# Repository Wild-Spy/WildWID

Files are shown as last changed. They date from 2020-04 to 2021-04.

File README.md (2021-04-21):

# WildWID
An open-source active RFID system for wildlife research

## Requirements
Some device firmware is written in C and requires the AVR/Atmel Studio IDE - https://www.microchip.com/mplab/avr-support/avr-and-sam-downloads-archive

Some device firmware is written in C and requires the IAR Embedded Workbench for 8051 IDE - https://www.iar.com/iar-embedded-workbench/#!?architecture=8051

Programming software is written in Visual Basic and requires the Microsoft Visual Studio IDE - https://visualstudio.microsoft.com

## Repository Structure
The WildWID repository is organised around the two components of the WildWID system: tags and loggers. Within the `Logger` and `Tag` folders you will find two sub-folders:

* Device firmware: contains firmware for the respective device.
* Production: contains the schematics and bill of materials required for PCB fabrication.

Within the `PC_Software` folder you will find multiple sub-folders containing the enduser software required to configure, test, and deploy tags and loggers.

## Further Information
A more detailed overview of WildWID and its use in wildlife biology is covered in: 

Rafiq, K., Appleby, R.G., Edgar, J.P., Jordan, N.R., Radford, C., Smith, B., Dexter, C.E., Jones, D.N., Blacker, A.R.F., and Cochrane, M., 'WildWID: An open-source active RFID system for wildlife research', *Methods in Ecology and Evolution*, in publication.



## License
This project is licensed under the terms of the GNU General Public License v3.0. See [LICENSE](LICENSE) for details.

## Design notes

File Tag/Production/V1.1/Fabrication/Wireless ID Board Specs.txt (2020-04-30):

Wireless ID Board Specifications

Layers: 		4
Thickness: 		0.6mm
Blind/Burried Vias: 	No
Surface Finish:		HAL Pb/Sn
Copper Finish:		1oz
Solder Mask:		Both Sides
Silk Screen:		Both Sides
Min Trace:		6mil
Min Hole:		12mil
PCB Material:		FR4

Gerber Files:
Bottom Copper Layer 	- Wireless ID.GBL
Bottom Solder Mask 	- Wireless ID.GBS
Bottom Silkscreen 	- Wireless ID.GBO
Internal Plane 1	- Wireless ID.GP1
Internal Plane 2	- Wireless ID.GP2
Top Copper Layer	- Wireless ID.GTL
Top Solder Mask		- Wireless ID.GTS
Top Silkscreen		- Wireless ID.GTO
Board Outline		- Wireless ID.GKO

Also, for Solder Paste Stencils:
(Copies of these files are also included in the 'Assembly Files' folder)
Top Paste Layer		- Wireless ID.GTP
Bottom Paste Layer	- Wireless ID.GBP

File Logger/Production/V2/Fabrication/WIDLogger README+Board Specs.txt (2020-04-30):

Wireless ID Board Specifications

Layers: 		2
Thickness: 		1.6mm
Surface Finish:	HAL Pb/Sn
Copper Finish:	1oz
Solder Mask:	Both Sides
Silk Screen:	Top Only
Min Trace:		6mil
Min Hole:		12mil
PCB Material:	FR4

Gerber Files:
Bottom Copper Layer	- WIDLogger.GBL
Bottom Solder Mask 	- WIDLogger.GBS
Top Copper Layer	- WIDLogger.GTL
Top Solder Mask		- WIDLogger.GTS
Top Silkscreen		- WIDLogger.GTO
Board Outline		- WIDLogger.GKO

NC Drill File:
WIDLogger.TXT

NOTE:
The Board Outline has two slots in it as is visible in the WIDLogger.GKO file.  These slots have a radius of 3.42mm.

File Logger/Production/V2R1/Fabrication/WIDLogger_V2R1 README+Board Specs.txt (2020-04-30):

Wireless ID Board Specifications

Layers: 		2
Thickness: 		1.6mm
Surface Finish:	HAL Pb/Sn
Copper Finish:	1oz
Solder Mask:	Both Sides
Silk Screen:	Top Only
Min Trace:		6mil
Min Hole:		12mil
PCB Material:	FR4

Gerber Files:
Bottom Copper Layer	- WIDLogger_V2R1.GBL
Bottom Solder Mask 	- WIDLogger_V2R1.GBS
Top Copper Layer	- WIDLogger_V2R1.GTL
Top Solder Mask		- WIDLogger_V2R1.GTS
Top Silkscreen		- WIDLogger_V2R1.GTO
Board Outline		- WIDLogger_V2R1.GKO

NC Drill File:
WIDLogger_V2R1.TXT

NOTE:
The Board Outline has two slots in it as is visible in the WIDLogger.GKO file.  These slots have a radius of 3.42mm.

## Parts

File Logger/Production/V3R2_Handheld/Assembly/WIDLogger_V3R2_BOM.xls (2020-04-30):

Bill of Materials
Source Data From: |  | WIDLogger V3R2
Project: |  | WIDLogger
Variant: |  | Logger Basic V3 |  |  |  |  |  |  |  | qty | 20
Creation Date: | 3/03/2013 | 9:32:15 PM
Print Date: | 2013-03-04 | 41337.54469
Designator | Value | Description | Footprint | Manufacturer 1 | Manufacturer Part Number 1 | Supplier 1 | Supplier Part Number 1 | Lead Free/RoHS | Quantity | Supplier Unit Price 1 | Supplier Order Qty 1 | Supplier Subtotal 1 | Supplier Currency 1
B1 |  | 0404 Balun for CC2500 | 0404 | Anaren | BD2425N50ATI | Digi-Key | 1173-1065-1-ND | RoHS | 1 | $0.47 | 20 | $9.36 | USD
C1, C2 | 15pF | Capacitor | 0603 | Murata Electronics North America | GRM1885C1H150JA01D | Digi-Key | 490-1407-1-ND | RoHS | 2 | $0.04 | 40 | $1.64 | USD
C3, C4, C5, C6, C8, C26 | 100nF | Capacitor | 0603 | Yageo | CC0603ZRY5V9BB104 | Digi-Key | 311-1343-1-ND | RoHS | 6 | $0.01 | 120 | $1.44 | USD
C11, C16 | 220pF | Capacitor | 0402 | Murata Electronics North America | GRM1555C1H221JA01D | Digi-Key | 490-1293-1-ND | RoHS | 2 | $0.03 | 40 | $1.24 | USD
C9 | 0R | Jumper | 402 | Yageo | RC0402JR-070RL | Digi-Key | 311-0.0JRCT-ND | RoHS | 1 | $0.01 | 20 | $0.24 | USD
C12, C13, C14, C17 | 100nF | Capacitor | 0402 | Murata Electronics North America | GRM155R61A104KA01D | Digi-Key | 490-1318-1-ND | RoHS | 4 | $0.01 | 80 | $0.80 | USD
C15 | 6.8pF | Capacitor | 0402 | Johanson Technology Inc | 500R07S6R8CV4T | Digi-Key | 712-1291-1-ND | RoHS | 1 | $0.15 | 20 | $3.00 | USD
C18, C29 | 15pF | Capacitor | 0402 | Murata Electronics North America | GRM1555C1H150JZ01D | Digi-Key | 311-1017-1-ND | RoHS | 2 | $0.00 | 40 | $0.00 | USD
C19, C23 | 10uF | Capacitor | 1206 | Taiyo Yuden | TMK316BJ106KL-T | Digi-Key | 587-1337-1-ND | RoHS | 2 | $0.25 | 40 | $10.00 | USD
C20 | 1uF | Capacitor | 0603 | Murata Electronics North America | GRM188F51E105ZA12D | Digi-Key | 490-3895-1-ND | RoHS | 1 | $0.07 | 20 | $1.40 | USD
C21 | 22uF | Capacitor | 1210 | TDK Corporation | C3225X7R1C226K250AC | Digi-Key | 445-3945-1-ND | RoHS | 1 | $0.72 | 20 | $14.40 | USD
C22 | 1500uF | Polarized Capacitor (Radial) | Radial | United Chemi-Con | EKZE250ELL152MK25S | Digi-Key | 565-1682-ND | RoHS | 1 | $1.21 | 20 | $24.20 | USD
C24 | 10nF | Capacitor | 0603 | Murata Electronics North America | GRM188R71C103KA01D | Digi-Key | 490-1525-1-ND | RoHS | 1 | $0.05 | 20 | $0.98 | USD
C30 | 1uF | Capacitor | 0805 | TDK Corporation | C2012X5R1C105K085AA | Digi-Key | 445-7632-1-ND | RoHS | 1 | $0.09 | 20 | $1.80 | USD
D2 |  | Diode - Regular | DO-214AC, SMA | Micro Commercial Co | ES1D-TP | Digi-Key | ES1D-TPCT-ND | RoHS | 1 | $0.30 | 20 | $6.00 | USD
D5, D6 |  | Diode - Schottky | SC-79 | Fairchild Semiconductor | RB520S30 | Digi-Key | RB520S30CT-ND | RoHS | 2 | $0.15 | 40 | $6.00 | USD
FB1 |  | Ferrite Bead | 0603 | Murata Electronics North America | BLM18AG102SN1D | Digi-Key | 490-1015-1-ND | RoHS | 1 | $0.08 | 20 | $1.60 | USD
J1 |  | U.FL | U.FL | Hirose Electric Co Ltd | U.FL-R-SMT(10) | Digi-Key | H9161CT-ND | RoHS | 1 | $1.41 | 20 | $28.20 | USD
L3 | 10nH | Inductor | 0402 | TDK Corporation | MLK1005S10NJ | Digi-Key | 445-1467-1-ND | RoHS | 1 | $0.05 | 20 | $1.00 | USD
L4 | 6.8uH | Inductor | SMD 8x8x4mm | Taiyo Yuden | NR8040T6R8N | Digi-Key | 587-2000-1-ND | RoHS | 1 | $0.40 | 20 | $8.00 | USD
L5 | Bead | Inductor | 0402 | Murata Electronics North America | BLM15HG601SN1D | Digi-Key | 490-3998-1-ND | RoHS | 1 | $0.19 | 20 | $3.80 | USD
MCU_STAT, TX | Red | LED | 0603 | OSRAM Opto Semiconductors Inc | LS Q971-KN-1 | Digi-Key | 475-3016-1-ND | RoHS | 2 | $0.07 | 40 | $2.72 | USD
Q1, Q6 |  | N-MOSFET | SOT-23 | NXP Semiconductors | BSH103,215 | Digi-Key | 568-5013-1-ND | RoHS | 2 | $0.38 | 40 | $15.20 | USD
R1, R16, R17 | 270R | Resistor | 0603 | Stackpole Electronics Inc | RMCF0603JT270R | Digi-Key | RMCF0603JT270RCT-ND | RoHS | 3 | $0.01 | 60 | $0.60 | USD
R2 | 9.53k | Resistor | 0603 | Panasonic Electronic Components | ERJ-3EKF9531V | Digi-Key | P9.53KHCT-ND | RoHS | 1 | $0.01 | 20 | $0.20 | USD
R3 | 499R | Resistor | 0603 | Panasonic Electronic Components | ERJ-3EKF4990V | Digi-Key | P499HCT-ND | RoHS | 1 | $0.01 | 20 | $0.20 | USD
R4 | 56k | Resistor | 0402 | Panasonic Electronic Components | ERJ-2RKF5602X | Digi-Key | P56.0KLCT-ND | RoHS | 1 | $0.10 | 20 | $2.00 | USD
R5, R6, R10 | 1M | Resistor | 0603 | Yageo | RC0603FR-071ML | Digi-Key | 311-1.00MHRCT-ND | RoHS | 3 | $0.01 | 60 | $0.60 | USD
R15, R35 | 0R | Resistor | 0603 | Stackpole Electronics Inc | RMCF0603ZT0R00 | Digi-Key | RMCF0603ZT0R00CT-ND | RoHS | 2 | $0.01 | 40 | $0.40 | USD
R13 | 4.7k | Resistor | 0603 | Stackpole Electronics Inc | RMCF0603JT4K70 | Digi-Key | RMCF0603JT4K70CT-ND | RoHS | 1 | $0.02 | 20 | $0.40 | USD
R14 | 10K | Resistor | 0603 | Stackpole Electronics Inc | RMCF0603JT10K0 | Digi-Key | RMCF0603JT10K0CT-ND | RoHS | 1 | $0.02 | 20 | $0.40 | USD
RX | Green | LED | 0603 | OSRAM Opto Semiconductors Inc | LG Q971-KN-1 | Digi-Key | 475-1409-1-ND | RoHS | 1 | $0.07 | 20 | $1.36 | USD
U1 |  | Microcontroller | 44-TQFP | Atmel | ATXMEGA32A4-AU | Digi-Key | ATXMEGA32A4-AU-ND | RoHS | 1 | $3.69 | 25 | $92.25 | USD
U3 |  | SPI Serial Flash Memory | 8-VDFN | Micron Technology Inc | M25P64-VME6TG | Digi-Key | M25P64-VME6TGCT-ND | RoHS | 1 | $2.66 | 20 | $53.16 | USD
U4 |  | Wireless transceiver IC | 20-VFQFN | Texas Instruments | CC2500RTKR | Digi-Key | 296-19586-1-ND | RoHS | 1 | $3.61 | 20 | $72.20 | USD
U5 |  | Buck Regulator | 16-QFN | Texas Instruments | TPS62111RSAT | Digi-Key | 296-20670-1-ND | RoHS | 1 | $3.83 | 20 | $76.62 | USD
U6 |  | FTDI USB-RS232 Converter | 28-SSOP | FTDI | FT232RL | Digi-Key | 768-1007-1-ND | RoHS | 1 | $4.05 | 20 | $81.00 | USD
U10 |  | Buffer | SC-70 | ON Semiconductor | M74VHC1G126DFT1G | Digi-Key | M74VHC1G126DFT1GOSCT-ND | RoHS | 1 | $0.33 | 20 | $6.60 | USD
USB-Cable |  | USB Cable | Cable | Molex Connector Corporation | 88738-8200 | Digi-Key | WM17105-ND | RoHS | 1 | $2.19 | 20 | $43.80 | USD
Y1 | 32768Hz | Crystal | 2-SMD 3.2x1.5mm | AVX Corp/Kyocera Corp | ST3215SB32768H5HPWAA | Digi-Key | 478-5428-1-ND | RoHS | 1 | $1.56 | 20 | $31.20 | USD
Y2 | 26MHz | Crystal | 4-SMD 5x3.2mm | Abracon Corporation | ABM3B-26.000MHZ-10-1-U-T | Digi-Key | 300-8219-1-ND | RoHS | 1 | $1.30 | 20 | $26.00 | USD
 |  |  |  |  |  |  |  |  | 61 | $30.68 |  | $632.01
Approved |  | Notes

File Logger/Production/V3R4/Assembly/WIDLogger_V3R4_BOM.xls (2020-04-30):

Designator | Footprint | Value | Description | Manufacturer 1 | Manufacturer Part Number 1 | Supplier 1 | Supplier Part Number 1 | Quantity | Supplier Unit Price 1 | Supplier Order Qty 1 | Supplier Subtotal 1 | Supplier Currency 1
B1 | Bauln0404 |  | 0404 Balun for CC2500 | Anaren | BD2425N50ATI | Digi-Key | 1173-1065-1-ND | 1 | 0.46 | 65 | 29.74 | AUD
B2 | 0433BM15A0001E |  | 430/433 MHz Impedance Matched Balun/LPF Integrated Component for T.I. Chipsets: CC1100, CC1101, CC110L, CC1111, CC1130, CC1131, CC1150, CC1151, CC113L, CC115L, CC430 and RF430. | Johanson Technology Inc. | 0433BM15A0001E | Digi-Key | 712-1540-1-ND | 1 | 1.04 | 65 | 67.38 | AUD
C1, C2 | CAP0603 | 15pF | Capacitor | Murata Electronics North America | GRM1885C1H150JA01D | Digi-Key | 490-1407-1-ND | 2 | 0.04 | 130 | 5.2 | AUD
C3, C4, C5, C6, C7, C26 | CAP0603 | 100nF | Capacitor, Capacitor - Non-polarised | Yageo | CC0603ZRY5V9BB104 | Digi-Key | 311-1343-1-ND | 6 | 0.01 | 390 | 3.73 | AUD
C9, C10 | 0402 | 0R | Capacitor - Non-polarised | Yageo | RC0402JR-070RL | Digi-Key | 311-0.0JRCT-ND | 2 | 0.01 | 130 | 1.01 | AUD
C11, C16, C28, C46 | 0402 | 220p | Capacitor - Non-polarised | Murata Electronics North America | GRM1555C1H221JA01D | Digi-Key | 490-1293-1-ND | 4 | 0.02 | 260 | 3.97 | AUD
C12, C13, C14, C17, C36, C40, C45, C47 | 0402 | 100n | Capacitor - Non-polarised | Murata Electronics North America | GRM155R61A104KA01D | Digi-Key | 490-1318-1-ND | 8 | 0.01 | 520 | 6.3 | AUD
C15 | 0402 | 6.8p | Capacitor - Non-polarised | Johanson Technology Inc. | 500R07S6R8CV4T | Digi-Key | 712-1291-1-ND | 1 | 0.13 | 65 | 8.26 | AUD
C18, C29, C48, C49 | 0402 | 15p | Capacitor - Non-polarised | Yageo | CC0402JRNPO9BN150 | Digi-Key | 311-1017-1-ND | 4 | 0.01 | 260 | 1.92 | AUD
C19, C23 | CAP1206 | 10u | Capacitor - Non-polarised | Taiyo Yuden | TMK316BJ106KL-T | Digi-Key | 587-1337-1-ND | 2 | 0.14 | 130 | 18.43 | AUD
C20 | CAP0603 | 1u | Capacitor - Non-polarised | Murata Electronics North America | GRM188F51E105ZA12D | Digi-Key | 490-3895-1-ND | 1 | 0.06 | 65 | 3.74 | AUD
C21 | CAP1210 | 22uF | Capacitor - Non-polarised | TDK Corporation | C3225X7R1C226K250AC | Digi-Key | 445-3945-1-ND | 1 | 0.6 | 100 | 59.63 | AUD
C22 | Cap-5.0-12.5 | 1500uF | Polarized Capacitor (Radial) | United Chemi-Con | EKZE250ELL152MK25S | Digi-Key | 565-1682-ND | 1 | 0.98 | 65 | 63.57 | AUD
C24 | CAP0603 | 10nF | Capacitor | Murata Electronics North America | GRM188R71C103KA01D | Digi-Key | 490-1525-1-ND | 1 | 0.04 | 65 | 2.46 | AUD
C25, C30 | CAP0805 | 1u | Capacitor - Non-polarised | TDK Corporation | C2012X5R1C105K085AA | Digi-Key | 445-7632-1-ND | 2 | 0.06 | 130 | 7.93 | AUD
C35 | CAP0805 | 100n | Capacitor - Non-polarised | AVX Corporation | 08055C104JAT2A | Digi-Key | 478-3352-1-ND | 1 | 0.04 | 100 | 3.92 | AUD
C41, C43, C44 | CAP1206 | 10u | Capacitor - Non-polarised | TDK Corporation | C3216X5R1A106K160AB | Digi-Key | 445-4057-1-ND | 3 | 0.13 | 250 | 32.06 | AUD
C42 | CAPM3216X18N | 27u | Capacitor - Non-polarised | Nichicon | RVB1E270MNG | Digi-Key | 493-13848-1-ND | 1 | 1.83 | 65 | 118.78 | AUD
D2 | ES1X Diode |  | Diode - Regular | Micro Commercial Co | GS1J-LTP | Digi-Key | GS1J-LTPMSCT-ND | 1 | 0.26 | 65 | 17.19 | AUD
D5 | SOD-523F |  | Diode - Schottky | Fairchild Semiconductor | RB520S30 | Digi-Key | RB520S30CT-ND | 1 | 0.14 | 100 | 14.49 | AUD
D7 | DO-214AC |  | Diode - Schottky | Vishay Semiconductor Diodes Division | B240A-E3/61T | Digi-Key | B240A-E3/61TGICT-ND | 1 | 0.31 | 100 | 30.95 | AUD
FB1 | RES0603 |  |  | Murata Electronics North America | BLM18AG102SN1D | Digi-Key | 490-1015-1-ND | 1 | 0.09 | 65 | 6.01 | AUD
J1, J3, J4 | SMA+UFL |  | SMA + U.FL | Hirose Electric Co Ltd | U.FL-R-SMT(10) | Digi-Key | H9161CT-ND | 3 | 1.44 | 195 | 281.17 | AUD
J6 | Iridium 9602 Data |  | Iridium 9602 SBD Transceiver | Samtec Inc. | CLP-110-02-L-D | Digi-Key | SAM1155-10-ND | 1 | 6.96 | 65 | 452.14 | AUD
J7 | Iridium 9602 ANT |  | Iridium 9602 SBD Transceiver | SAMTEC | MMCX-P-P-H-ST-TH1 | Farnell | 2113293 | 1 | 7.31 | 65 | 475.15 | AUD
L2 | INDP139135X59N | 3.3uH | Inductor | Bourns Inc. | SRP1250-3R3M | Digi-Key | SRP1250-3R3MCT-ND | 1 | 1.64 | 65 | 106.69 | AUD
L3 | 0402 | 10nH | Inductor | TDK Corporation | MLK1005S10NJT000 | Digi-Key | 445-1467-1-ND | 1 | 0.06 | 65 | 3.61 | AUD
L4 | 8040Inductor | 6.8uH | Inductor | Taiyo Yuden | NR8040T6R8N | Digi-Key | 587-2000-1-ND | 1 | 0.49 | 65 | 32.1 | AUD
L5 | 0402 | Bead | Inductor | Yageo | RC0402JR-070RL | Digi-Key | 311-0.0JRCT-ND | 1 | 0.01 | 100 | 0.78 | AUD
L6 | 0402 |  | Inductor | Yageo | RC0402JR-070RL | Digi-Key | 311-0.0JRCT-ND | 1 | 0.01 | 100 | 0.78 | AUD
MCU_STAT, TX | CAP0603 | Red | Light-Emitting Diode, Typical INFRARED GaAs LED | OSRAM Opto Semiconductors Inc. | LS Q976-NR-1 | Digi-Key | 475-2512-1-ND | 2 | 0.15 | 130 | 19.33 | AUD
Q1, Q6 | SOT23 |  | N-Channel Enhancement Mode MOSFET | NXP Semiconductors | BSH103,215 | Digi-Key | 568-5013-1-ND | 2 | 0.28 | 130 | 36.67 | AUD
R1, R16, R17 | RES0603 | 270R | Resistor | Stackpole Electronics Inc. | RMCF0603JT270R | Digi-Key | RMCF0603JT270RCT-ND | 3 | 0.01 | 250 | 1.41 | AUD
R2 | RES0603 | 9.53k | Resistor | Panasonic Electronic Components | ERJ-3EKF9531V | Digi-Key | P9.53KHCT-ND | 1 | 0.02 | 65 | 1.05 | AUD
R3 | RES0603 | 499R | Resistor | Panasonic Electronic Components | ERJ-3EKF4990V | Digi-Key | P499HCT-ND | 1 | 0.02 | 65 | 1.05 | AUD
R4, R12 | 0402 | 56k | Resistor | Panasonic Electronic Components | ERJ-2RKF5602X | Digi-Key | P56.0KLCT-ND | 2 | 0.02 | 130 | 2.04 | AUD
R5, R6, R10 | RES0603 | 1M | Resistor | Yageo | RC0603FR-071ML | Digi-Key | 311-1.00MHRCT-ND | 3 | 0.01 | 250 | 1.67 | AUD
R13 | RES0603 | 4.7k | Resistor | Stackpole Electronics Inc. | RMCF0603JT4K70 | Digi-Key | RMCF0603JT4K70CT-ND | 1 | 0.01 | 65 | 0.65 | AUD
R14 | RES0603 | 10K | Resistor | Stackpole Electronics Inc. | RMCF0603JT10K0 | Digi-Key | RMCF0603JT10K0CT-ND | 1 | 0.01 | 65 | 0.65 | AUD
R15, R21, R35 | RES0603 | 0R | Resistor | Stackpole Electronics Inc. | RMCF0603ZT0R00 | Digi-Key | RMCF0603ZT0R00CT-ND | 3 | 0.01 | 250 | 1.41 | AUD
R37 | RES0603 | 100k | Resistor | Yageo | RC0603FR-07100KL | Digi-Key | 311-100KHRCT-ND | 1 | 0.01 | 100 | 0.87 | AUD
RX | CAP0603 | Green | Typical INFRARED GaAs LED | Wurth Electronics Inc | 150060VS75000 | Digi-Key | 732-4980-1-ND | 1 | 0.34 | 65 | 22.37 | AUD
U1 | TQFP-44pin-0.8mm |  | Microcontroller with 32KB Primary Flash | Atmel | ATXMEGA32A4-AU | Digi-Key | ATXMEGA32A4-AU-ND | 1 | 7.89 | 65 | 512.72 | AUD
U2 | SO8N+SO8W |  | SPI Serial Flash Memory | Micron Technology Inc. | M25P16-VMN6TP | Digi-Key | M25P16-VMN6TPCT-ND | 1 | 1.15 | 65 | 74.95 | AUD
U4 | QFN20 |  | Wireless transceiver IC | Texas Instruments | CC2500RGPR | Digi-Key | 296-38562-1-ND | 1 | 4.89 | 65 | 317.67 | AUD
U5 | QFN16 - 0.65mm Pitch |  | 17V, 1.5A, Synchronous step down converter with high light load efficiency | Texas Instruments | TPS62111RSAT | Digi-Key | 296-20670-1-ND | 1 | 4.31 | 65 | 280.41 | AUD
U6 | SSOP28-0.65mm |  | FTDI USB-RS232 Converter | FTDI, Future Technology Devices International Ltd | FT232RL-REEL | Digi-Key | 768-1007-1-ND | 1 | 5.49 | 65 | 356.55 | AUD
U7 | QFN20 |  | Ultra low-power wireless applications operating in the 315/433/868/915 MHz ISM/SRD bands. | Texas Instruments | CC110LRGPR | Digi-Key | 296-35719-1-ND | 1 | 5.06 | 65 | 329 | AUD
U10 | SC-88A (SC-70-5/SOT-353) |  | Noninverting Tristate Buffer with Noniverting OE | ON Semiconductor | M74VHC1G126DFT1G | Digi-Key | M74VHC1G126DFT1GOSCT-ND | 1 | 0.21 | 100 | 21.16 | AUD
U12 | SOIC127P600-8N11 |  |  | Analog Devices Inc. | ADP2302ARDZ-5.0-R7 | Digi-Key | ADP2302ARDZ-5.0-R7CT-ND | 1 | 3.81 | 65 | 247.72 | AUD
USB | My_USB |  | USB-B Female Connector | On Shore Technology Inc. | USB-M26FTR | Digi-Key | ED2992CT-ND | 1 | 0.98 | 65 | 63.96 | AUD
Y1 | XTAL 32768Hz SMT3 |  | XTAL | AVX Corp/Kyocera Corp | ST3215SB32768H5HPWAA | Digi-Key | 478-5428-1-ND | 1 | 0.81 | 65 | 52.57 | AUD
Y2, Y3 | XTAL-ABM3B | 26MHz |  | Abracon LLC | ABM3B-26.000MHZ-10-1-U-T | Digi-Key | 300-8219-1-ND | 2 | 1.14 | 130 | 148.17 | AUD
 |  |  |  |  |  |  |  |  |  |  | 4353.14

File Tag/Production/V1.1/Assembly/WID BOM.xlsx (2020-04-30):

Manufacturer 1 | Manufacturer Part Number 1 | Comment | Designator | Footprint | Value | Quantity | Supplier Part Number | Unit Price | Currency | Cost in USD
LINX TECHNOLOGIES | ANT-2.45-CHP-T | Antenna | ANT1 | 2.45GHZ-CHP-ANT |  | 1 | ANT-2.45-CHPCT-ND | 1.296 | USD | $1.30
TAIYO YUDEN | JMK212BJ226MG-T | Cap Pol1 | C2 | CAP0805 | 47uF | 1 | 1463398 | 0.44 | AUD | $0.43
TAIYO YUDEN | TMK105BJ104KV-F | Cap | C3, C4, C5, C8 | 0402 | 100nF | 4 | 1611916 | 0.01 | AUD | $0.04
MULTICOMP | MCCA000093 | Cap | C6, C7 | 0402 | 12pF | 2 | 1758943 | 0.01 | AUD | $0.02
KEMET | C0402C333K4RACTU | cap | C9 | 0402 | 33nF | 1 | 1414591 | 0.04 | AUD | $0.04
TAIYO YUDEN | JMK107BJ475MA-T | cap | C10 | CAP0603 | 4.7uF | 1 | 1463379 | 0.12 | AUD | $0.12
KEMET | C0402C103K3RACTU | cap | C11 | 0402 | 10nF | 1 | 1650806 | 0.02 | AUD | $0.02
AVX | 0402YC102KAT2A | cap | C12 | 0402 | 1nF | 1 | 1327660 | 0.04 | AUD | $0.04
JOHANSON TECHNOLOGY | 500R07S1R5BV4T | cap | C13 | 0402 | 1.5pF | 1 | 1650787 | 0.07 | AUD | $0.07
TAIYO YUDEN | UMK105CG010BW-F | cap | C14 | 0402 | 1.0pF | 1 | 1683591 | 0.01 | AUD | $0.01
KEMET | C0402C222K5RACTU | cap | C15 | 0402 | 2.2nF | 1 | 1414582 | 0.01 | AUD | $0.01
AVX | 04025A4R7CAT2A | cap | C16 | 0402 | 4.7pF | 1 | 1327640 | 0.04 | AUD | $0.04
KEMET | C0402C220J5GACTU | cap | C17, C18 | 0402 | 22pF | 2 | 1414580 | 0.01 | AUD | $0.02
ABRACON | ATFC-0402-3N9B | Inductor | L1 | 0402 | 3.9nH | 1 | 1628745 | 0.1 | AUD | $0.10
ABRACON | ATFC-0402-8N2B | Inductor | L2 | 0402 | 8.2nH | 1 | 1628753 | 0.1 | AUD | $0.10
ABRACON | ATFC-0402-2N7B | Inductor | L3 | 0402 | 2.7nH | 1 | 1628728 | 0.1 | AUD | $0.10
ROHM | SML-310LTT86N | LED2 | LED | CAP0603 |  | 1 | 1685062 | 0.16 | AUD | $0.16
TYCO ELECTRONICS / NEOHM | CRG0402J1K0 | Res1 | R2 | 0402 | 1K | 1 | 1174154 | 0.09 | AUD | $0.09
MULTICOMP | MC 0.0625W 0402 1% 22K | Res3 | R4 | 0402 | 22K | 1 | 1358077 | 0.13 | AUD | $0.13
Atmel | ATMEGA88PA-MU | ATMEGA168P | U2 | 32M1-A_L |  | 1 | ATMEGA88PA-MU-ND | 3.57 | USD | $3.57
Nordic | nRF24L01+ | nRF24L01+ | U3 | QFN50P400X400X95-20N |  | 1 | COM-00690 | 3.5 | USD | $3.15
AVX Corporation | ST3215SB32768H5HPWAA | XTAL | Y1 | XTAL RTC SMT | 32.768kHz | 1 | 478-5428-1-ND | 1.5 | USD | $1.50
TXC CORPORATION | 7B-16.000MAAJ-T | XTAL | Y2 | XTAL-SPK-5032 | 16MHz | 1 | 887-1104-1-ND | 1.13 | USD | $1.13
 |  |  |  |  |  |  |  |  | Total Cost: | $12.16
 |  |  |  |  |  |  |  |  | +17% | $14.23
1 AUD = | 0.97666 | USD

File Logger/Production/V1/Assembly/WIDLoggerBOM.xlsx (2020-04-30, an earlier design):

Comment | Designator | Value | Footprint | Manufacturer 1 | Manufacturer Part Number 1 | Qty Per Board | Supplier 1 | Supplier Part Number 1 | Qty for 20 Boards | Supplier Unit Price | Supplier Subtotal 1 | Supplier Currency | Subtotal (USD)
Cap | C1, C2 | 15pF | CAP0603 | MURATA | GRM1885C1H150JA01D | 2 | Farnell | 8819823 | 50 | $0.020 | $0.80 | AUD | $0.78
Cap Pol1 | C3 | 33uF | CAPPR2-5x6.8 | ILLINOIS CAPACITOR | 336CKS050M | 1 | Farnell | 1203665 | 20 | $0.080 | $1.62 | AUD | $1.58
Cap | C4, C5, C6, C7, C8, C19, C21 | 100nF | CAP0603 | MULTICOMP | MCCA000255 | 7 | Farnell | 1759122 | 140 | $0.010 | $1.82 | AUD | $1.78
cap | C9 | 33nF | 0402 | KEMET | C0402C333K4RACTU | 1 | Farnell | 1414591 | 20 | $0.040 | $0.80 | AUD | $0.78
cap | C10 | 4.7uF | CAP0603 | TAIYO YUDEN | JMK107BJ475MA-T | 1 | Farnell | 1463379 | 20 | $0.120 | $2.36 | AUD | $2.30
cap | C11 | 10nF | 0402 | KEMET | C0402C103K3RACTU | 1 | Farnell | 1650806 | 20 | $0.020 | $0.40 | AUD | $0.39
cap | C12 | 1nF | CAP0402 | AVX | 0402YC102KAT2A | 1 | Digi-Key | 311-1352-1-ND | 20 | $0.011 | $0.22 | USD | $0.22 | *
cap | C13 | 1.5pF | 0402 | JOHANSON TECHNOLOGY | 500R07S1R5BV4T | 1 | Farnell | 1650787 | 20 | $0.070 | $1.30 | AUD | $1.27
cap | C14 | 1.0pF | 0402 | TAIYO YUDEN | UMK105CG010BW-F | 1 | Farnell | 1683591 | 20 | $0.010 | $0.20 | AUD | $0.20
cap | C15 | 2.2nF | 0402 | KEMET | C0402C222K5RACTU | 1 | Farnell | 1414582 | 20 | $0.010 | $0.24 | AUD | $0.23
cap | C16 | 4.7pF | 0402 | AVX | 04025A4R7CAT2A | 1 | Farnell | 1327640 | 20 | $0.040 | $0.82 | AUD | $0.80
cap | C17, C18 | 22pF | 0402 | KEMET | C0402C220J5GACTU | 2 | Farnell | 1414580 | 40 | $0.010 | $0.48 | AUD | $0.47
Cap | C20 | 10nF | CAP0603 | MULTICOMP | MCCA000238 | 1 | Farnell | 1759104 | 100 | $0.010 | $1.30 | AUD | $1.27
Cap | C22 | 10uF | 1210TantCap | AVX | TPSB106K016R0800 | 1 | Farnell | 1135112 | 20 | $1.190 | $23.80 | AUD | $23.23
Cap | C23 | 1uF | CAP0805 | MULTICOMP | MCCA000552 | 1 | Farnell | 1759432 | 100 | $0.040 | $4.20 | AUD | $4.10
FerriteBead | FB1 |  | RES0603 | MURATA | BLM18AG102SN1D | 1 | Farnell | 1515671 | 20 | $0.030 | $0.56 | AUD | $0.55
SMA-Con | J1 |  | SMA-CON | ChangHong | SMA Female RP PCB Mount | 1 | Sparkfun | WRL-00592 | 20 | $1.760 | $35.20 | USD | $35.20
USB-B | J2 |  | USBB-CON-TH | FCI | 61729-1010BLF | 1 | Farnell | 1632146 | 20 | $0.870 | $17.40 | AUD | $16.98
Inductor | L1 | 3.9nH | 0402 | ABRACON | ATFC-0402-3N9B | 1 | Farnell | 1628745 | 20 | $0.100 | $2.00 | AUD | $1.95
Inductor | L2 | 8.2nH | 0402 | ABRACON | ATFC-0402-8N2B | 1 | Farnell | 1628753 | 20 | $0.100 | $2.00 | AUD | $1.95
Inductor | L3 | 2.7nH | 0402 | ABRACON | ATFC-0402-2N7B | 1 | Farnell | 1628728 | 20 | $0.100 | $2.00 | AUD | $1.95
Header 2 | P2 |  | Screw Terminal 0.2" | On Shore Technology Inc | OSTTA024163 | 1 | Digi-Key | ED2580-ND | 20 | $0.250 | $5.04 | USD | $5.04
Res3 | R1, R2 | 270R | RESC1608L | YAGEO (PHYCOMP) | RT0603FRE07270RL | 2 | Digi-Key | RMCF0603JT270R | 40 | $0.017 | $0.68 | USD | $0.68 | *
Res3 | R3 | 4k7 | RESC1608L | VISHAY DRALORIC | CRCW06034K70FKEA | 1 | Farnell | 1469807 | 20 | $0.020 | $0.40 | AUD | $0.39
Res3 | R4 | 22K | 0402 | MULTICOMP | MC 0.0625W 0402 1% 22K | 1 | Farnell | 1358077 | 50 | $0.130 | $6.40 | AUD | $6.25
Res3 | R5 | 10k | RESC1608L | VISHAY DRALORIC | CRCW060310K0JNEA | 1 | Farnell | 1469749 | 20 | $0.070 | $1.30 | AUD | $1.27
LED0 | RX |  | CAP0603 | KINGBRIGHT | KP-1608SGC | 1 | Farnell | 1226392 | 20 | $0.135 | $2.70 | AUD | $2.64
LED0 | TX |  | CAP0603 | OSRAM | LSR976 | 1 | Farnell | 8529833 | 20 | $0.177 | $3.54 | AUD | $3.46 |  | not supplier numbers, manufacturer numbers:
SPI Serial Flash Memory | U2 |  | S08 | Numonyx/ST Micro | M25P16-VMN6TP | 1 | Digi-Key | M25P16-VMN6TPCT-ND | 20 | $1.710 | $34.20 | USD | $34.20 | Alternatives: | M25PE16-VMW6TGCT-ND | SST26VF016-80-5I-S2AE | SST25VF016B-75-4I-S2AF
nRF24L01+ | U3 |  | QFN50P400X400X95-20N | Nordic | nRF24L01+ | 1 | Sparkfun | COM-00690 | 20 | $3.500 | $70.00 | USD | $70.00 |  | (Digikey) | (Mouser) | (Element 14)
FT232RL | U4 |  | SSOP28-0.65mm | FTDI | FT232RL | 1 | Sparkfun | COM-00650 | 20 | $4.050 | $81.00 | USD | $81.00
LP2981-3.3V | U5 |  | SOT23-5P285X122-5N | Texas Instruments | LP2981-33DBVR | 1 | Digi-Key | 296-17360-1-ND | 20 | $0.880 | $17.60 | USD | $17.60
XTAL | Y1 |  | XTAL 32768Hz SMT3 | AVX Corporation | ST3215SB32768H5HPWAA | 1 | Digi-Key | 478-5428-1-ND | 20 | $1.350 | $27.00 | USD | $27.00
16MHz | Y2 | 16.000 MHz | XTAL-SPK-5032 | Abracon Corporation | ABM3B-16.000MHZ-B2-T | 1 | Digi-Key | 535-9122-1-ND | 20 | $1.630 | $32.50 | USD | $32.50
 |  |  |  |  |  |  |  |  |  |  |  | 20 Boards: | $380.00
 |  |  |  |  |  |  |  |  |  |  |  | 1 Board: | $19.00
AUD to USD conversion:
1 AUD = | 0.976 | USD

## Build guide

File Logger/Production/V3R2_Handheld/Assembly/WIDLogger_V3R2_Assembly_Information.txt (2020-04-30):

WIDLogger_V3R2 Assembly Information:

Quantity requested: 20 Assembled Boards

PCB Size: 				74x100mm (approx)
Two sided: 				No
# SMT Parts: 			55
# TH Parts: 			1
# Fine Pitch Parts:		2
# BGA/QFN/Leadless:		3
Smallest Part Size: 	0402
Leaded/LeadFree:		Lead-Free

Files
BOM File:				WIDLogger_V2R2_BOM_to_Bittele.xls
Top Solder Paste File:	WIDLogger_V3R2.GTP
Readme File:			WIDLogger_V3R2_Assembly_Information.txt (this file)

Extra Info:
The orientation of parts Y1 and Y2 are not important, therefore Pin1 is not marked.
Orientation is not important for any Capicitor except for C22.
For D2, Pin1 (marked with dot) is the cathode.
For D6 and D5, the cathode is marked as follows:  
    ___   
 K |___  A

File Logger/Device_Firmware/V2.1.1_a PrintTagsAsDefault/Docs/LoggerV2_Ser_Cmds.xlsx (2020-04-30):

Cmd | Cmd | Name | Input 1 Name | Input 1 Type | Input 2 Name | Input 2 Type | Input 3 Name | Input 3 type | Output 1 Name | Output 1 Type | Output 2 Name | Output 2 Type | Output 3 Name | Output 3 Type
0 | 00 | Get_DevTypeID |  |  |  |  |  |  | DevTypeID | uint16_t
1 | 01 | Get_AllRecordsFast
2 | 02 | Cmd_SaveDummy_Record | ID | uint32_t | Time | uint8_t[6] |  |  | Address | uint32_t
3 | 03 | Get_EntryAtAddress | Address | uint32_t |  |  |  |  | ID | uint32_t | Time | uint8_t[5] | Flags | uint8_t
4 | 04 | Cmd_EraseDataflash | Check | uint16_t
5 | 05 | Cmd_PollDataFlashErased |  |  |  |  |  |  | Result | uint8_t
6 | 06 | Get_Version |  |  |  |  |  |  | ProductName | uint8_t[50] | HardwareVersion | uint8_t[10] | SoftwareVersion | uint8_t[10]
7 | 07 | Get_RecordCount |  |  |  |  |  |  | RecordCount | uint32_t
8 | 08 | Set_RecordCount | RecordCount | uint32_t
9 | 09 | Get_DateTime |  |  |  |  |  |  | Time | uint8_t[6]
10 | 0A | Set_DateTime | Time | uint8_t[6]
11 | 0B | Get_RFChan |  |  |  |  |  |  | RFChan | uint8_t
12 | 0C | Set_RFChan | RFChan | uint8_t
13 | 0D | Get_RFID |  |  |  |  |  |  | RFID | uint8_t[5]
14 | 0E | Set_RFID | RFID | uint8_t[5]
15 | 0F | Get_RFFilter |  |  |  |  |  |  | RFFiter | uint32_t
16 | 10 | Set_RFFilter | RFFiter | uint32_t
17 | 11 | Get_SendDataGPRSPeriod |  |  |  |  |  |  | Time | uint8_t[6]
18 | 12 | Set_SendDataGPRSPeriod | Time | uint8_t[6]
19 | 13 | Get_SendDataGPRSNext |  |  |  |  |  |  | Time | uint8_t[6]
20 | 14 | Set_SendDataGPRSNext | Time | uint8_t[6]
21 | 15 | Get_LoggerName |  |  |  |  |  |  | LoggerName | uint8_t[20]
22 | 16 | Set_LoggerName | LoggerName | uint8_t[20]
23 | 17 | Get_VerboseMode |  |  |  |  |  |  | VerboseMode | uint8_t
24 | 18 | Set_VerboseMode | VerboseMode | uint8_t
25 | 19 | Cmd_GM862 | cmd_ID | uint8_t
26 | 1A | Cmd_GM862BridgeMode
27 | 1B | Get_GPRSVals
28 | 1C | Set_GPRSVals
29 | 1D | Get_EmailToAddress |  |  |  |  |  |  | EmailToAddress | uint8_t[60]
30 | 1E | Set_EmailToAddress | EmailToAddress | uint8_t[60]

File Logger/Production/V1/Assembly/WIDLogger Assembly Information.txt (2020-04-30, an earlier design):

WIDLogger Assembly Information:

PCB Size: 		60x41mm
Two sided: 		No
# SMT Parts: 		40
# TH Parts: 		3
Smallest Part Size: 	0402

Extra Info:
The following parts should not be fitted:
C24
P3
J3
PDI
U1
(Note that these have been removed from the pick and place file)

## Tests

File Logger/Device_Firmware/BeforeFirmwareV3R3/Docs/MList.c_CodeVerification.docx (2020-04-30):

# Code Verification

Verified | File | Function
| MList.c | mx_err_t mList_Init(void);
| MList.c | mx_err_t mList_AddItem(uint32_t* ID, uint32_t* Addy, RTC_Time_t* LastTime);
| MList.c | mx_err_t mList_RemoveItem(uint16_t Address);
| MList.c | mx_err_t mList_RemoveItemWithID(uint32_t remID);
| MList.c | mx_err_t mList_Item(uint16_t Index, ListStruct_t** RetVal);
| MList.c | mx_err_t mList_ItemWithID(uint32_t ID, ListStruct_t** RetVal)
| MList.c | uint16_t mList_GetCount(void);

# 1 MList.c Functions

## 1.1 Initialise List Function

Synopsis

mx_err_t mList_Init(void);

dddd

Description/Reasoning | Input | Expected Output | Actual Output | Pass/Fail
Class 1 – Visual Code Inspection
Class 2 –Practical Use Test | Code has been used | No Problems Caused

## 1.2 Send Email Function

Synopsis

GM862_err_t GM862_SendEmail(void);

Description/Reasoning | | Input | Expected Output | Actual Output | Pass/Fail
Class 1 –
1.1
Class 2 –Practical Test | | Simulated use in the field.
2.1 | First Send | Device with 393 logs on it, scheduled to send email at 10:53AM on 28-09-2011. Send Period set to 10 minutes, all other properties set up correctly (email address, GPRS settings) (set to split email every 100 logs) | 4 emails received with all data. | 4 emails received with all data | Pass
2.2 | Second Send | Simulated some tag pickups. 0x1DC logs total now. | One email with log 0x1C9 through to log 0x1DC | One email with log 0x1C9 through to log 0x1DC | Pass
2.3 | Third Send | Simulated some tag pickups. 0x1F3 logs total now. | One email with log 0x1DC through to log 0x1F3 | One email with log 0x1DC through to log 0x1F3 | Pass
2.4 | Fourth Send | No more tags pickups simulated. 0x1F5 logs total now. | One email with log 0x1F3 through to log 0x1F5 | One email with log 0x1F3 through to log 0x1F5 | Pass
2.5 | Repeated entries

## 1.3 ListUpdate

Synopsis

Not a specific function but the whole List-Update system.

Description/Reasoning | | Input | Expected Output | Actual Output | Pass/Fail
Class 1 – Random Entries
1.1 | Random Tags 1 | Randomly sending 8 different tags. | Exported to csv, sorted by tag number. Separate into groups of logs from single tags. Each start log has an accompanying stop log and vice versa. There are never two start or two stop logs from one tag in a row (ordered by time). | Exported to csv, sorted by tag number. Separate into groups of logs from single tags. Each start log has an accompanying stop log and vice versa. There are never two start or two stop logs from one tag in a row (ordered by time). | Pass
Class 2 – Full List
2.1 | Overflow | Set List max size to 5. Sent 8 different tags. | The first 5 go into list. Other sent tags after that just get a ‘start’ and no accompanying ‘stop’. | The first 5 go into list. Other sent tags after that just get a ‘start’ and no accompanying ‘stop’. | Pass

## 1.4 Wait For Main Battery on Startup Function

NOT IMPLEMENTED!!!! – Main battery MUST be plugged in before backup battery!

Synopsis

No function, just the way it works.

Description/Reasoning | | Input | Expected Output | Actual Output | Pass/Fail
Class 1 – Startup Tests
1.1 | Power Good | Main battery is already connected on start-up. Tested using Debugger. | Startup and operation as normal. | Startup and operation as normal. | Pass
1.2 | Power Bad | Main battery is not connected on start-up. Tested using Debugger. | Does necessary startup tasks then enters battery backup mode. Executes ‘Startup’ instructions in main ‘awake’ loop when getting power. Record count is retrieved in wakefrombatbak() function. | Does necessary startup tasks then enters battery backup mode. Executes ‘Startup’ instructions in main ‘awake’ loop when getting power. Record count is retrieved in wakefrombatbak() function. | Pass
Class 2 –

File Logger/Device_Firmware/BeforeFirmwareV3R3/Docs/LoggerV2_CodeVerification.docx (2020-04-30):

# Code Verification

Verified | Source File | ID
| WIDLogV2.c | 1
| Strings.c | 2
| MX_SerComms.c | 3
| MX_GM862.c | 4
| MX_NRF24L01.c | 5
| MX_SerFlash.c | 6
| MX_USART.c | 7
| MX_RTC.c | 8
| MList.c | 9
| TC_driver.c | 10
| eeprom_driver.c | 11
| Clksys_driver.c | 12
| WIDLogV2.h | 1a
| Strings.h | 2a
| MX_SerComms.h | 3a
| MX_GM862.h | 4a
| MX_NRF24L01.h | 5a
| MX_SerFlash.h | 6a
| MX_USART.h | 7a
| MX_RTC.h | 8a
| MList.h | 9a
| TC_driver.h | 10a
| eeprom_driver.h | 11a
| Clksys_driver.h | 12a

# 1 WIDLogV2.c Functions

Verified | Source File | Function
| WIDLogV2.c | int main(void);
| WIDLogV2.c | ISR(PORTB_INT0_vect)
| WIDLogV2.c | ISR(TCC0_OVF_vect)
| WIDLogV2.c | void MainLoop_BatBackup_NoBat_Mode()
| WIDLogV2.c | void MainLoop_BatBackup_LoBat_Mode()
| WIDLogV2.c | void WaitForMainBattery()
| WIDLogV2.c | void SetupHardware()
| WIDLogV2.c | uint8_t EnterBatBakMode(uint8_t Reason)
| WIDLogV2.c | uint8_t WakeFromBatBakMode()
| WIDLogV2.c | float CheckBatteryVoltage()
| WIDLogV2.c | void CalibrateADCOffset()
| WIDLogV2.c | int ADCRead(uint8_t SAMP)
| WIDLogV2.c | void RTCWakeChecks()
| WIDLogV2.c | void ReelInTheYears()
| WIDLogV2.c | void ShowMenu()
| WIDLogV2.c | void doRFWork(uint8_t dispLvl)
| WIDLogV2.c | void UpdateTagList()
| WIDLogV2.c | uint8_t saveRecord(RTC_Time_t* mTime, uint32_t* ID)
| WIDLogV2.c | uint8_t loadRecord(uint32_t RecordNo, RTC_Time_t* mTime, uint32_t* ID)
| WIDLogV2.c | uint8_t RecordToFlash(RTC_Time_t* mTime, uint32_t ID, uint8_t Flags)
| WIDLogV2.c | void StartTim10ms(uint16_t Time)
| WIDLogV2.c | void StopTim10ms()
| WIDLogV2.c | void save_PC(void)
| WIDLogV2.c | uint8_t ReadCalibrationByte( uint8_t index )
| WIDLogV2.c | void FilterStr2Mask(char* filtStr)
| WIDLogV2.c | uint32_t FindRecordCount()
| WIDLogV2.c | void SetClkSpeed(uint8_t speed)

## 1.1 Main Function

Synopsis

int main(void);

Description/Reasoning | Input | Expected Output | Actual Output | Pass/Fail
Class 1 – Visual Code Inspection
Class 2 –Practical Use Test | Code has been used | No Problems Caused

## 1.2 Main Function

Synopsis

ISR(PORTB_INT0_vect)

This function is called when the power good pin on the DC-DC switching converter goes low, indicating that the main battery has been removed. It’s job is to put the logger into a low-power ‘battery backup’ mode if appropriate and to return to a different

Description/Reasoning | Input | Expected Output | Actual Output | Pass/Fail
Class 1 – Visual Code Inspection
Class 2 –Practical Use Test | Code has been used | No Problems Caused

# 2 Strings.c Functions

Verified | Source File | Function
| WIDLogV2.c | int main(void);
| WIDLogV2.c | ISR(PORTB_INT0_vect)

## 2.1 Main Function

Synopsis

mx_err_t mList_Init(void);

Description/Reasoning | | Input | Expected Output | Actual Output | Pass/Fail
Class 1 – Visual Code Inspection
1.1
Class 2 –Practical Use Test
2.1

# 3 MX_SerComms.c Functions

Verified | Source File | Function
| MX_SerComms.c | int main(void);
| MX_SerComms.c | ISR(PORTB_INT0_vect)

## 3.1 Main Function

Synopsis

mx_err_t mList_Init(void);

Description/Reasoning | | Input | Expected Output | Actual Output | Pass/Fail
Class 1 – Visual Code Inspection
1.1
Class 2 –Practical Use Test
2.1

# 4 MX_GM862.c Functions

Verified | Source File | Function
| MX_GM862.c | int main(void);
| MX_GM862.c | ISR(PORTB_INT0_vect)

## 4.1 Main Function

Synopsis

mx_err_t mList_Init(void);

Description/Reasoning | | Input | Expected Output | Actual Output | Pass/Fail
Class 1 – Visual Code Inspection
1.1
Class 2 –Practical Use Test
2.1

# 5 MX_NRF24L01.c Functions

Verified | Source File | Function
| MX_NRF24L01.c | int main(void);
| MX_NRF24L01.c | ISR(PORTB_INT0_vect)

## 5.1 Main Function

Synopsis

mx_err_t mList_Init(void);

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

# 6 MX_SerFlash.c Functions

Verified | Source File | Function
| MX_SerFlash.c | int main(void);
| MX_SerFlash.c | ISR(PORTB_INT0_vect)

## 6.1 Main Function

Synopsis

mx_err_t mList_Init(void);

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

# 7 MX_USART.c Functions

Verified | Source File | Function
| MX_USART.c | int main(void);
| MX_USART.c | ISR(PORTB_INT0_vect)

## 7.1 Main Function

Synopsis

mx_err_t mList_Init(void);

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

# 8 MX_RTC.c Functions

Verified | Source File | Function
| MX_RTC.c | int main(void);
| MX_RTC.c | ISR(PORTB_INT0_vect)

## 8.1 Main Function

Synopsis

mx_err_t mList_Init(void);

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

# 9 MList.c Functions

Verified | Source File | Function
| MList.c | int main(void);
| MList.c | ISR(PORTB_INT0_vect)

## 9.1 Main Function

Synopsis

mx_err_t mList_Init(void);

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

# 10 TC_driver.c Functions

Verified | Source File | Function
| TC_driver.c | int main(void);
| TC_driver.c | ISR(PORTB_INT0_vect)

## 10.1 Main Function

Synopsis

mx_err_t mList_Init(void);

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

# 11 MX_NRF24L01.c Functions

Verified | Source File | Function
| MX_NRF24L01.c | int main(void);
| MX_NRF24L01.c | ISR(PORTB_INT0_vect)

## 11.1 Main Function

Synopsis

mx_err_t mList_Init(void);

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

# 12 MX_NRF24L01.c Functions

Verified | Source File | Function
| MX_NRF24L01.c | int main(void);
| MX_NRF24L01.c | ISR(PORTB_INT0_vect)

## 12.1 Main Function

Synopsis

mx_err_t mList_Init(void);

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

# 13 Other tests

## 13.1 Send Email Function

Synopsis

GM862_err_t GM862_SendEmail(void);

Description/Reasoning | | Input | Expected Output | Actual Output | Pass/Fail
Class 1 –
1.1
Class 2 –Practical Test | | Simulated use in the field.
2.1 | First Send | Device with 393 logs on it, scheduled to send email at 10:53AM on 28-09-2011. Send Period set to 10 minutes, all other properties set up correctly (email address, GPRS settings) (set to split email every 100 logs) | 4 emails received with all data. | 4 emails received with all data | Pass
2.2 | Second Send | Simulated some tag pickups. 0x1DC logs total now. | One email with log 0x1C9 through to log 0x1DC | One email with log 0x1C9 through to log 0x1DC | Pass
2.3 | Third Send | Simulated some tag pickups. 0x1F3 logs total now. | One email with log 0x1DC through to log 0x1F3 | One email with log 0x1DC through to log 0x1F3 | Pass
2.4 | Fourth Send | No more tags pickups simulated. 0x1F5 logs total now. | One email with log 0x1F3 through to log 0x1F5 | One email with log 0x1F3 through to log 0x1F5 | Pass
2.5 | Repeated entries

## 13.2 ListUpdate

Synopsis

Not a specific function but the whole List-Update system.

Description/Reasoning | | Input | Expected Output | Actual Output | Pass/Fail
Class 1 – Random Entries
1.1 | Random Tags 1 | Randomly sending 8 different tags. | Exported to csv, sorted by tag number. Separate into groups of logs from single tags. Each start log has an accompanying stop log and vice versa. There are never two start or two stop logs from one tag in a row (ordered by time). | Exported to csv, sorted by tag number. Separate into groups of logs from single tags. Each start log has an accompanying stop log and vice versa. There are never two start or two stop logs from one tag in a row (ordered by time). | Pass
Class 2 – Full List
2.1 | Overflow | Set List max size to 5. Sent 8 different tags. | The first 5 go into list. Other sent tags after that just get a ‘start’ and no accompanying ‘stop’. | The first 5 go into list. Other sent tags after that just get a ‘start’ and no accompanying ‘stop’. | Pass

## 13.3 Wait For Main Battery on Startup Function

NOT IMPLEMENTED!!!! – Main battery MUST be plugged in before backup battery!

Synopsis

No function, just the way it works.

Description/Reasoning | | Input | Expected Output | Actual Output | Pass/Fail
Class 1 – Startup Tests
1.1 | Power Good | Main battery is already connected on start-up. Tested using Debugger. | Startup and operation as normal. | Startup and operation as normal. | Pass
1.2 | Power Bad | Main battery is not connected on start-up. Tested using Debugger. | Does necessary startup tasks then enters battery backup mode. Executes ‘Startup’ instructions in main ‘awake’ loop when getting power. Record count is retrieved in wakefrombatbak() function. | Does necessary startup tasks then enters battery backup mode. Executes ‘Startup’ instructions in main ‘awake’ loop when getting power. Record count is retrieved in wakefrombatbak() function. | Pass
Class 2 –

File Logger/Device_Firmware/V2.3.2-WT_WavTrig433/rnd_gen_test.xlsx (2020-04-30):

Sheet: logger_data_raw
0 | 2010-01-01 | 0:01:04 | 1000001 | Start | -80 | 0 | 2
1 | 2010-01-01 | 0:01:04 | 1000001 | Start | -87 | 0 | NONE
2 | 2010-01-01 | 0:01:07 | 1000001 | Start | -90 | 0 | NONE
3 | 2010-01-01 | 0:02:13 | 1000001 | Start | -68 | 0 | 3
4 | 2010-01-01 | 0:03:26 | 1000001 | Start | -75 | 0 | 1
6 | 2010-01-01 | 0:00:11 | 1000001 | Start | -73 | 0 | 2
7 | 2010-01-01 | 0:01:14 | 1000001 | Start | -72 | 0 | 3
8 | 2010-01-01 | 0:01:14 | 1000001 | Start | -72 | 0 | NONE
9 | 2010-01-01 | 0:14:37 | 1000001 | Start | -75 | 0 | 1
10 | 2010-01-01 | 0:14:47 | 1000001 | Start | -68 | 0 | 2
11 | 2010-01-01 | 0:15:54 | 1000001 | Start | -66 | 0 | 3
12 | 2010-01-01 | 0:15:54 | 1000001 | Start | -63 | 0 | NONE
13 | 2010-01-01 | 0:15:57 | 1000001 | Start | -65 | 0 | NONE
14 | 2010-01-01 | 0:15:57 | 1000001 | Start | -64 | 0 | 2
15 | 2010-01-01 | 0:15:59 | 1000001 | Start | -67 | 0 | NONE
16 | 2010-01-01 | 0:16:00 | 1000001 | Start | -68 | 0 | NONE
17 | 2010-01-01 | 0:16:01 | 1000001 | Start | -69 | 0 | NONE
19 | 2010-01-01 | 0:00:24 | 1000001 | Start | -73 | 0 | 5
20 | 2010-01-01 | 0:00:24 | 1000001 | Start | -72 | 0 | NONE
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

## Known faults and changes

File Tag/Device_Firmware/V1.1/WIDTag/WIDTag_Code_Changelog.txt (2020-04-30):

WID Tag Changelog
Created: 10/08/2011
Updated: 18/10/2011
Author: Matthew Cochrane
Company: Wild Spy

Version: V0.2.2
	- Code Finished: 18/10/2011
	- Workshop Implementation Date: ??/10/2011
	- Firmware: WIDTagV0.2.2.hex 
	- EEPROM:	WIDTag_EEPROM_V0.2.hex
	- Fuses: H-0xD6, L-0xE2, E-0xF9(0x01)
	
	NOTES:
	- MCU MUST still be a pico-power device (for BOD Disable feature). ATmega48PA/88PA/168PA/328P 
	
	TODO:
	- Test this version in the workshop and see if we still get ESD problems when potting the WIDs.
	
	Description:
	- Fifth code revision at workshop.  This code revision was written for two main purposes:
		1. To counter still pervailant issues with the LED ON problem which are causing the device to 
		   stop transmitting once potted.
		2. To try out some Test Driven Development code writing techniques.  
	- A new NRF24L01+ controller library was written to accomplish both of these requirements.  The new 
	  NRF24L01P Library was written in eclipse using Test Driven Development techniques.
		- The LED ON issue that was fixed in V0.2.1 was still buggy.  It sometimes caused the unit to get stuck 
		  in a loop where if it got hit my too much static, every transmit thereafter would time out.  Instead of
		  showing a solid LED ON, the unit would simply not transmit.  
		- The above problem is improved upon in this version of the code.  In V0.2.1, the Tx timeout was based
		  on the RTC timer and would only timeout after at leas one second had elapsed.  Now the Tx subroutime
		  uses its own dedicated timer (TC0) which will timeout after 4ms (and yes this IS long enough, search 
		  the datasheet for '4ms').  
		- The new library boasts other improvements as well, the main one is that it has been very well tested
		  using TDD techniques.
		- The library is much better written then the previous version.  The code file should never need to be 
		  modified (unless there is a bug).  It makes use of function pointers and link-time dependancies on
		  low level IO functions so that they are not stuck in the main code file.  This results in low code
		  coupling, easier to read code and more reliable code.
	
	Changes:
	- New NRF24L01P Library written in eclipse using Test Driven Development techniques.
	- The BOD activation voltage was changed from 2.7V to 1.8V.
	- The 'N' command from the menu now reads all of the registers from the nordic chip and prints them out.
	- The random feature was modified it no longer uses rand() but is based on the tag's ID.  Has not been 
	  empirically tested but some basic TDD tests show that it should work fine.
		
--------------------------------------------------------------------------------------------------------------------

Version: V0.2.1
	- Code Finished: 13/08/2011
	- Workshop Implementation Date: ??/08/2011
	- Firmware: WIDTagV0.2.1.hex 
	- EEPROM:	WIDTag_EEPROM_V0.2.hex
	- Fuses: H-0xDD, L-0xE2, E-0xF9(0x01)
	
	NOTES:
	- MCU MUST now be a pico-power device (for BOD Disable feature). ATmega48PA/88PA/168PA/328P 
	
	TODO:
	- Test that the batteries still get decent life with 2.7V BOD reset.  Consider changing to 1.8V BOD reset?
	
	Description:
	- Fourth code revision at workshop.  This code revision was written to fix the LED ON issue with the WIDs.
	The previous code version (V0.2.1) was very short lived.  The first day it was brought into the workshop 
	it was discovered that it had not resolved the LED ON issue which it was supposed to.  The software BOD
	that was implemented in the previous version was left incorporated.  The LED ON problem was ultimately
	overcome by first finally understanding its cause which could be traced back to its origin after creating. 
	a repeatible test the caused the fault.  This test was performed by unleashing a large static discharge was 
	the WID's antenna while the MCU was asleep and this consistantly yeilded the same result (~90% of the time). 
	Nothing would happen until the WID woke up (which was at the correct time) and then the LED would turn on
	solid and remain on indefinitely.  The root cause of this problem was that the nordic chip (nRF24L01+) was 
	being reset (?) by a static discharge while the MCU was asleep and its SRAM contents was lost.  This meant 
	that the chip wasn't properly configured next time the MCU woke up. When it did, the MCU sent tx data to the
	nordic chip, told it to transmit the data and then waited for the nordic chip to flag that it had transmitted
	that data however because it wasn't set up properly, the nordic chip never set this flag and therefore the 
	MCU would be stuck in an infinite loop.  
	- The situation was remedied by adding a timeout while the MCU waits for the TX complete flag to be set.  If
	this timout occurs then we know that the nordic chip was probably reset, so the MCU then re-initialises it.

	Changes:
	- Fixed LED ON problem caused by static discharge.  Timeout implemented in function NRF24L01_TX_PAYLOAD.
	- Changes from V0.2.0 listed below as they are very recent and because V0.2.0 should never be used!
		- Fuses changed so that BOD is activated (2.7V reset cutoff).
		- Implemented software BOD feature (BOD on in active mode, off in sleep mode).
		- EEPROM locations shifted.  WID_ID moved from address 0x00, all addresses shifted by 0x10 and addresses 
		  spread out more so no two variables are directly adjacent.
		- New EEPROM file (WIDTag_EEPROM_V0.2.hex), also changed file format from raw to intel hex.
		
--------------------------------------------------------------------------------------------------------------------

Version: V0.2.0
	- Code Finished: 10/08/2011
	- Workshop Implementation Date: 12/08/2011
	- Firmware: WIDTagV0.2.hex 
	- EEPROM:	WIDTag_EEPROM_V0.2.hex
	- Fuses: H-0xDD, L-0xE2, E-0xF9
	
	NOTES:
	- LED ON PROBLEM STILL NOT FIXED!!! USE V0.2.1!! DO NOT USE THIS VERSION OF CODE!!!
	- MCU MUST now be a pico-power device (for BOD Disable feature). ATmega48PA/88PA/168PA/328P 
	- Found bugs in this version almost immediately once implemented in the workshop!
	
	TODO:
	- Test that the batteries still get decent life with 2.7V BOD reset.  Consider changing to 1.8V BOD reset?
	
	Description:
	- Third code revision at workshop.  This code revision was written to combat the problems we are experiencing
	with WIDs locking up (LED stuck on) and EEPROM values being erronously overwritten.  The theory is that these
	phenomenon are being caused by the microprocessor going rogue as a result of its power lines droping below its
	minimum operating voltage.  The Brown Out Detector on the ATMEGA88PA uses far too much power (20-30uA) to be a
	viable solution to this problem alone however on Pico-power devices (ATMEGA**P/ATMEGA**PA) there is a software
	BOD feature which allows the BOD to be enabled when the MCU is in active mode and disabled when it is in any
	sleep mode.  This greatly reduces the energy cost of having the BOD active to the point where it makes 
	essentially no difference to the devices average current consumption (<0.1% difference).  The BOD still does
	it's job as it's active in the MCUs active mode (is activated and stabilised BEFORE the MCU executes any 
	instructions) and does not need to be active in sleep mode as the CPU is not executing instructions and thus
	the chances of data corruption are greatly reduced.  It is still possible that some memory (RAM) locations 
	are corrupted while in sleep mode if the voltage drops too low.  Not sure HOW possible this is but it may
	be worth resetting the MCU once or twice a day in case of any corruption. 
	- The first byte in EEPROM is more prone to being overwritten if a power supply failure occurs.  Even though
	the chances of this happening are GREATLY reduced with the BOD enabled the EEPROM locations were shifted to
	further reduce the risk of this impornt data being corrupted.
	
	Changes:
	- Fuses changed so that BOD is activated (2.7V reset cutoff).
	- Implemented software BOD feature (BOD on in active mode, off in sleep mode).
	- EEPROM locations shifted.  WID_ID moved from address 0x00, all addresses shifted by 0x10 and addresses 
	  spread out more so no two variables are directly adjacent.
	- New EEPROM file (WIDTag_EEPROM_V0.2.hex), also changed file format from raw to intel hex.
	
--------------------------------------------------------------------------------------------------------------------
	
Version: V0.1.2
	- Code Finished: ??/??/2011
	- Workshop Implementation Date: ??/??/2011
	- Firmware: WIDTagV0.1.2.hex 
	- EEPROM:	WIDTag_EEPROM_V0.1.eeprom
	- Fuses: H-0xDF, L-0xE2, E-0xF9
	
	Description:
	- Second code revision at workshop.
	
	Changes:
	- Fixed LED-on problem (can't remember how.. update this when you remember!)
	
--------------------------------------------------------------------------------------------------------------------
	
Version: V0.1.1
	- Code Finished: ??/??/2011
	- Workshop Implementation Date: ??/??/2011
	- Firmware: WIDTagV0.1.1.hex 
	- EEPROM:	WIDTag_EEPROM_V0.1.eeprom
	- Fuses: H-0xDF, L-0xE2, E-0xF9
	
	Description:
	- First code revision.
	
	Changes:
	- Not sure... :s

--------------------------------------------------------------------------------------------------------------------
	
Version: V0.1.0
	- Firmware: WIDTagV0.1.0.hex 
	- EEPROM:	WIDTag_EEPROM_V0.1.eeprom
	- Fuses: H-0xDF, L-0xE2, E-0xF9
	
	Description:
	- Original code version (documented after the fact)

--------------------------------------------------------------------------------------------------------------------

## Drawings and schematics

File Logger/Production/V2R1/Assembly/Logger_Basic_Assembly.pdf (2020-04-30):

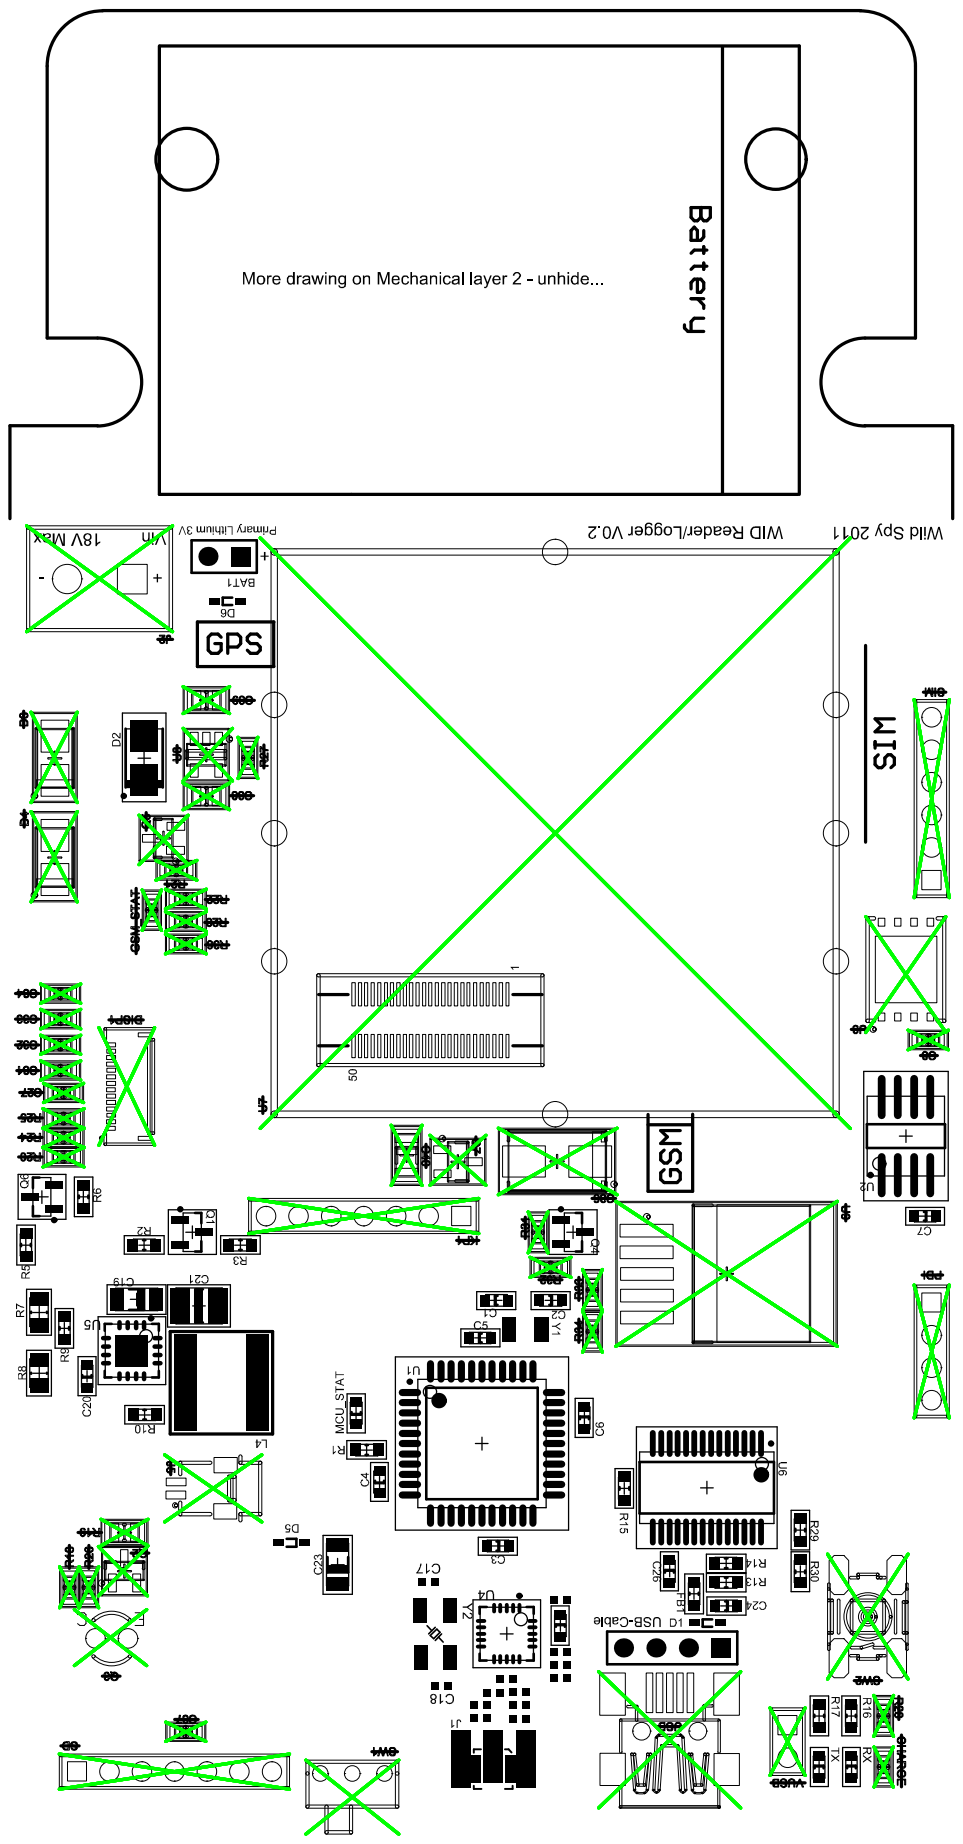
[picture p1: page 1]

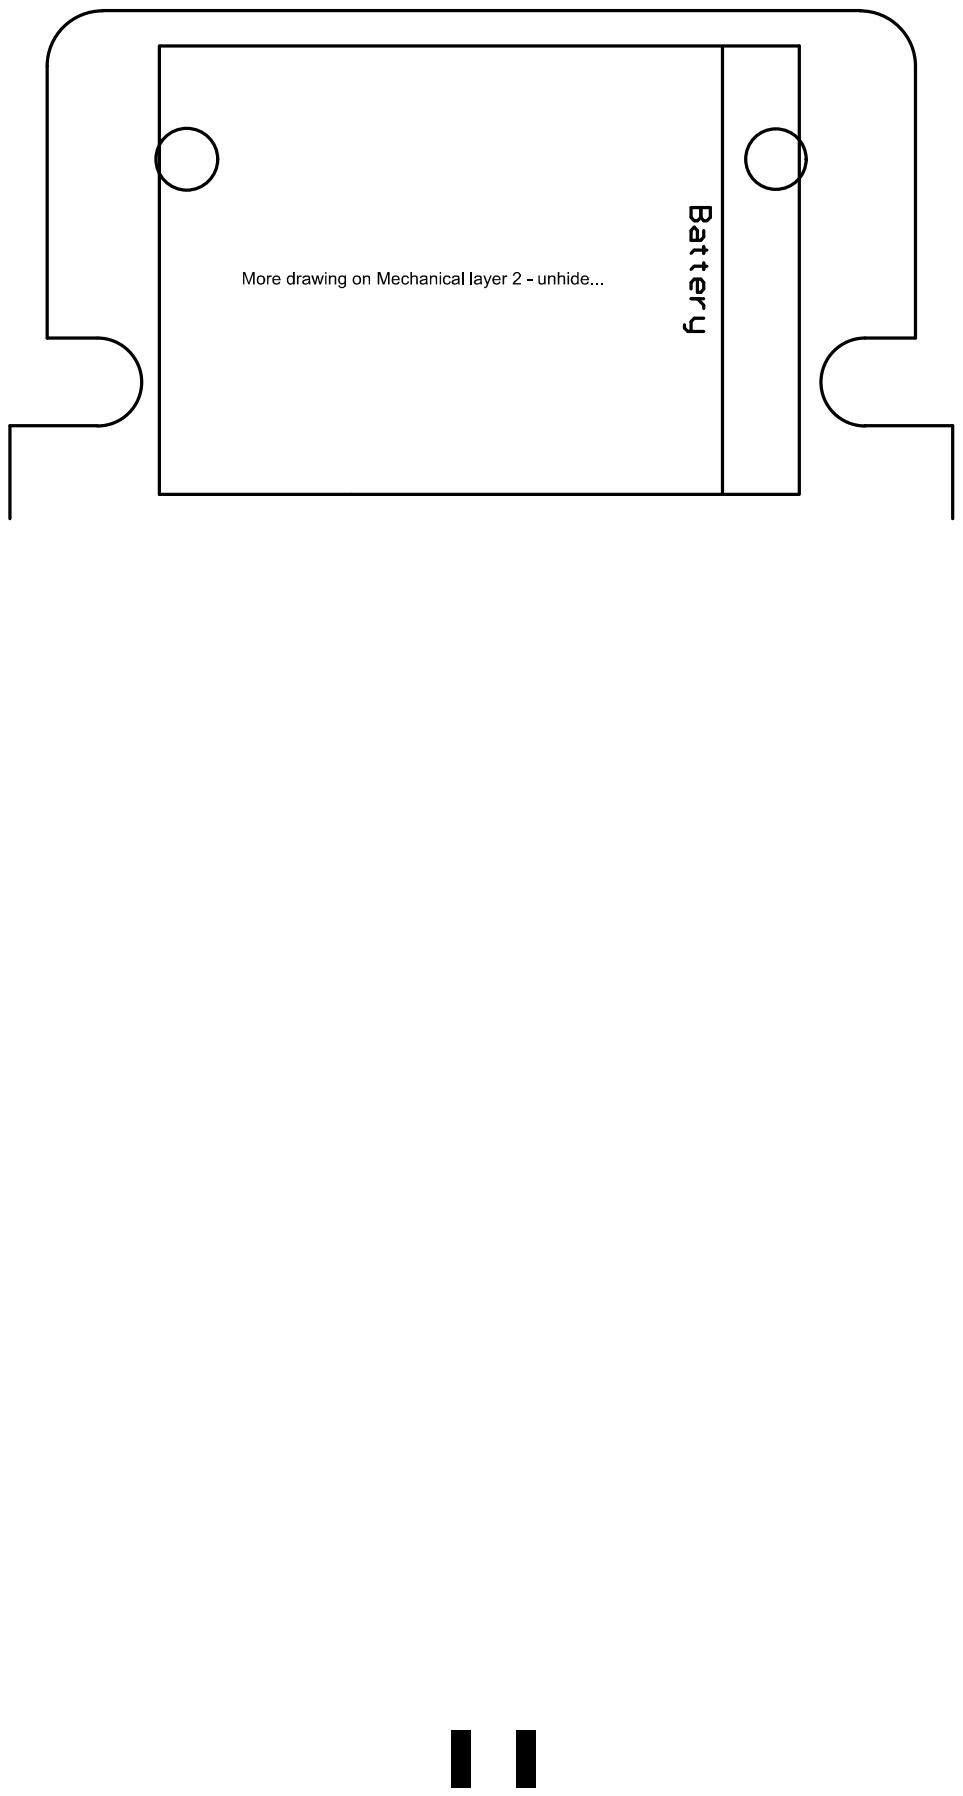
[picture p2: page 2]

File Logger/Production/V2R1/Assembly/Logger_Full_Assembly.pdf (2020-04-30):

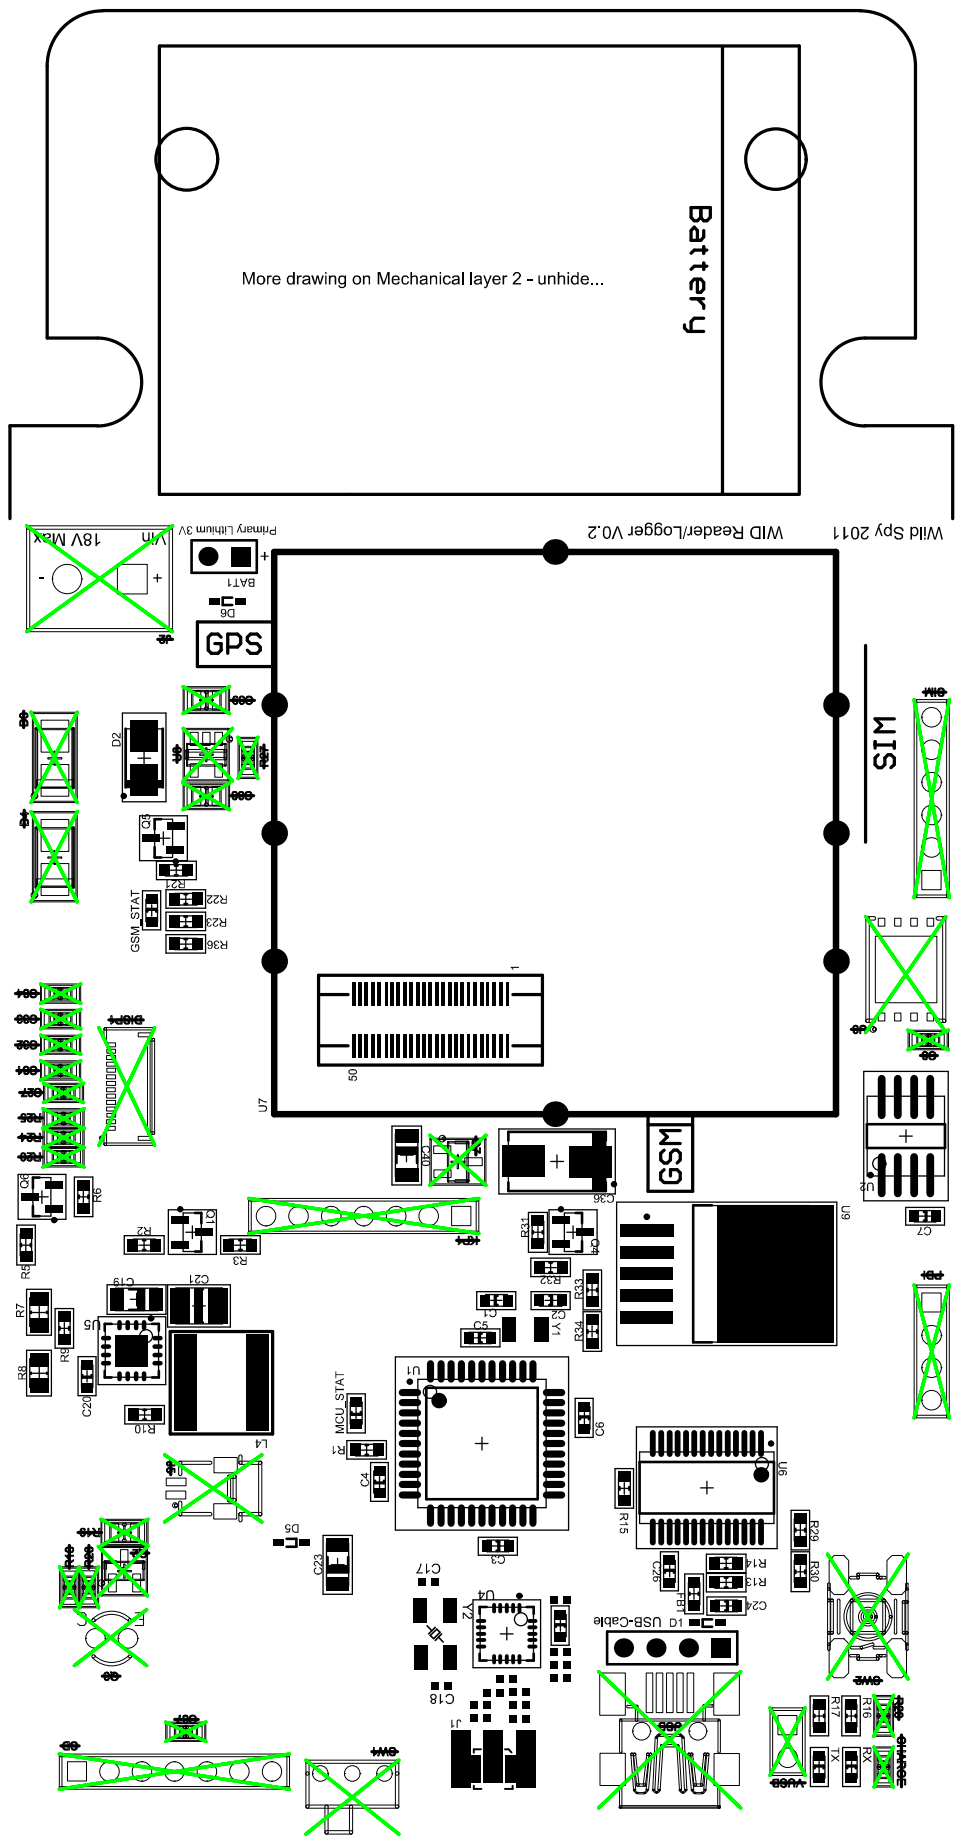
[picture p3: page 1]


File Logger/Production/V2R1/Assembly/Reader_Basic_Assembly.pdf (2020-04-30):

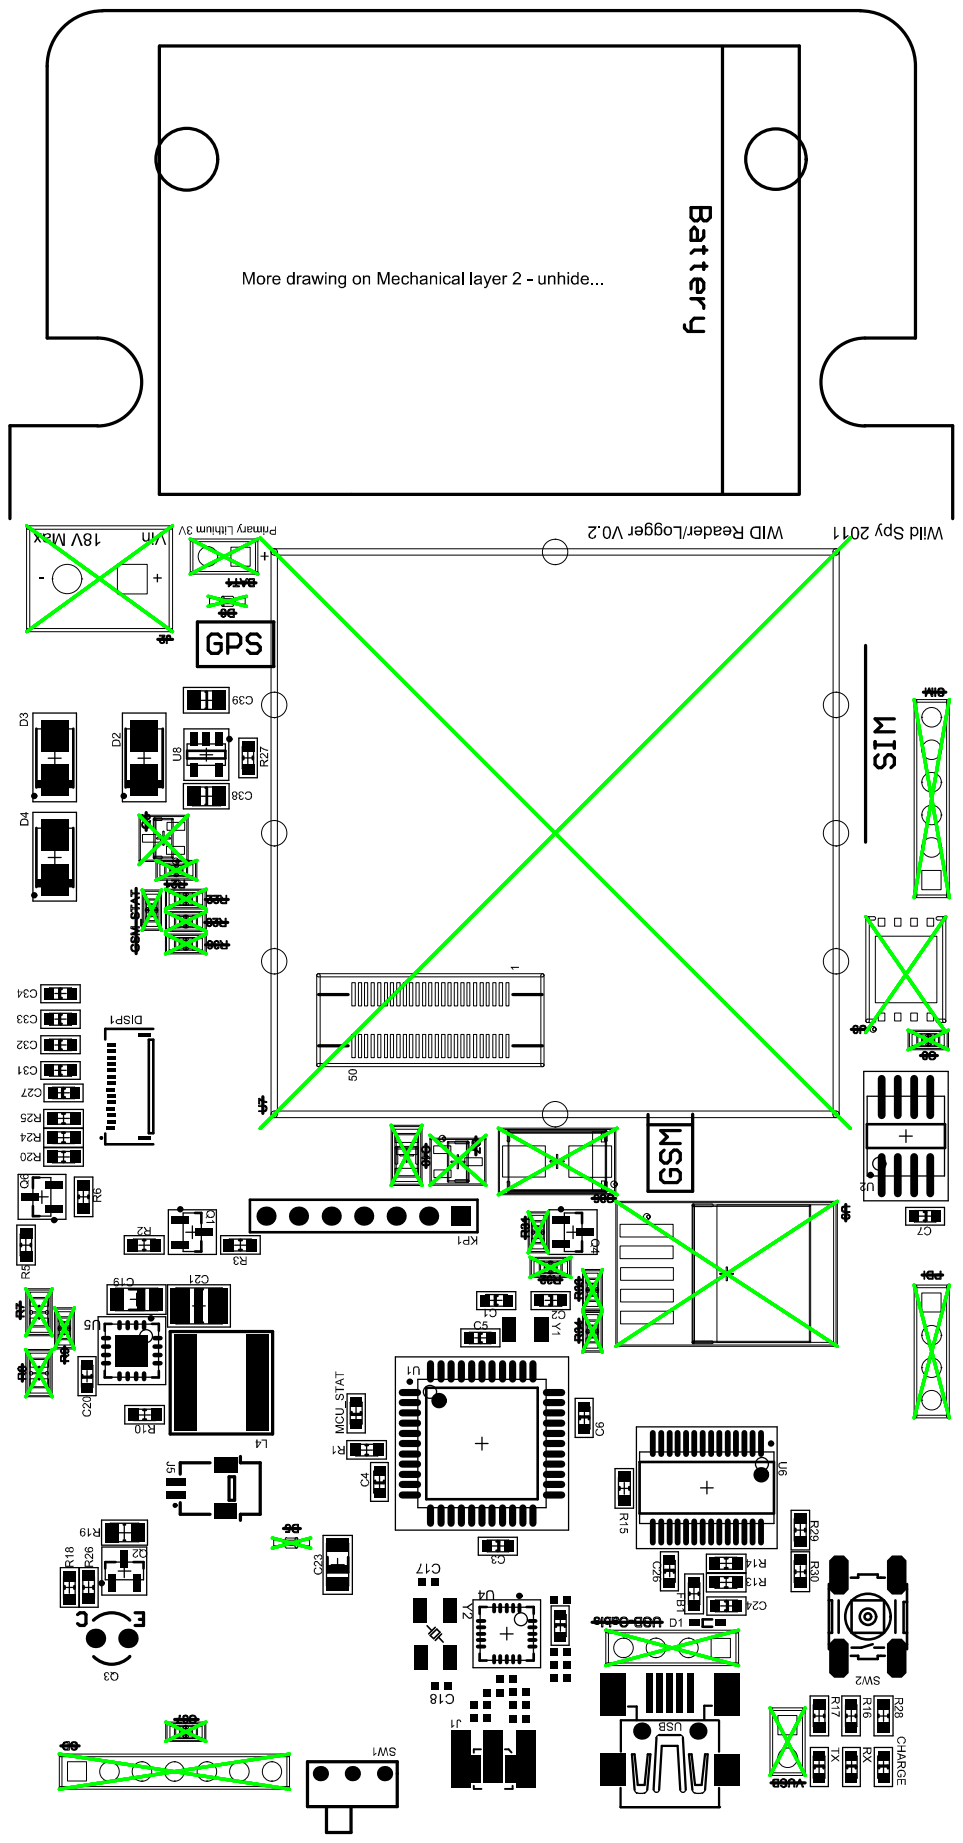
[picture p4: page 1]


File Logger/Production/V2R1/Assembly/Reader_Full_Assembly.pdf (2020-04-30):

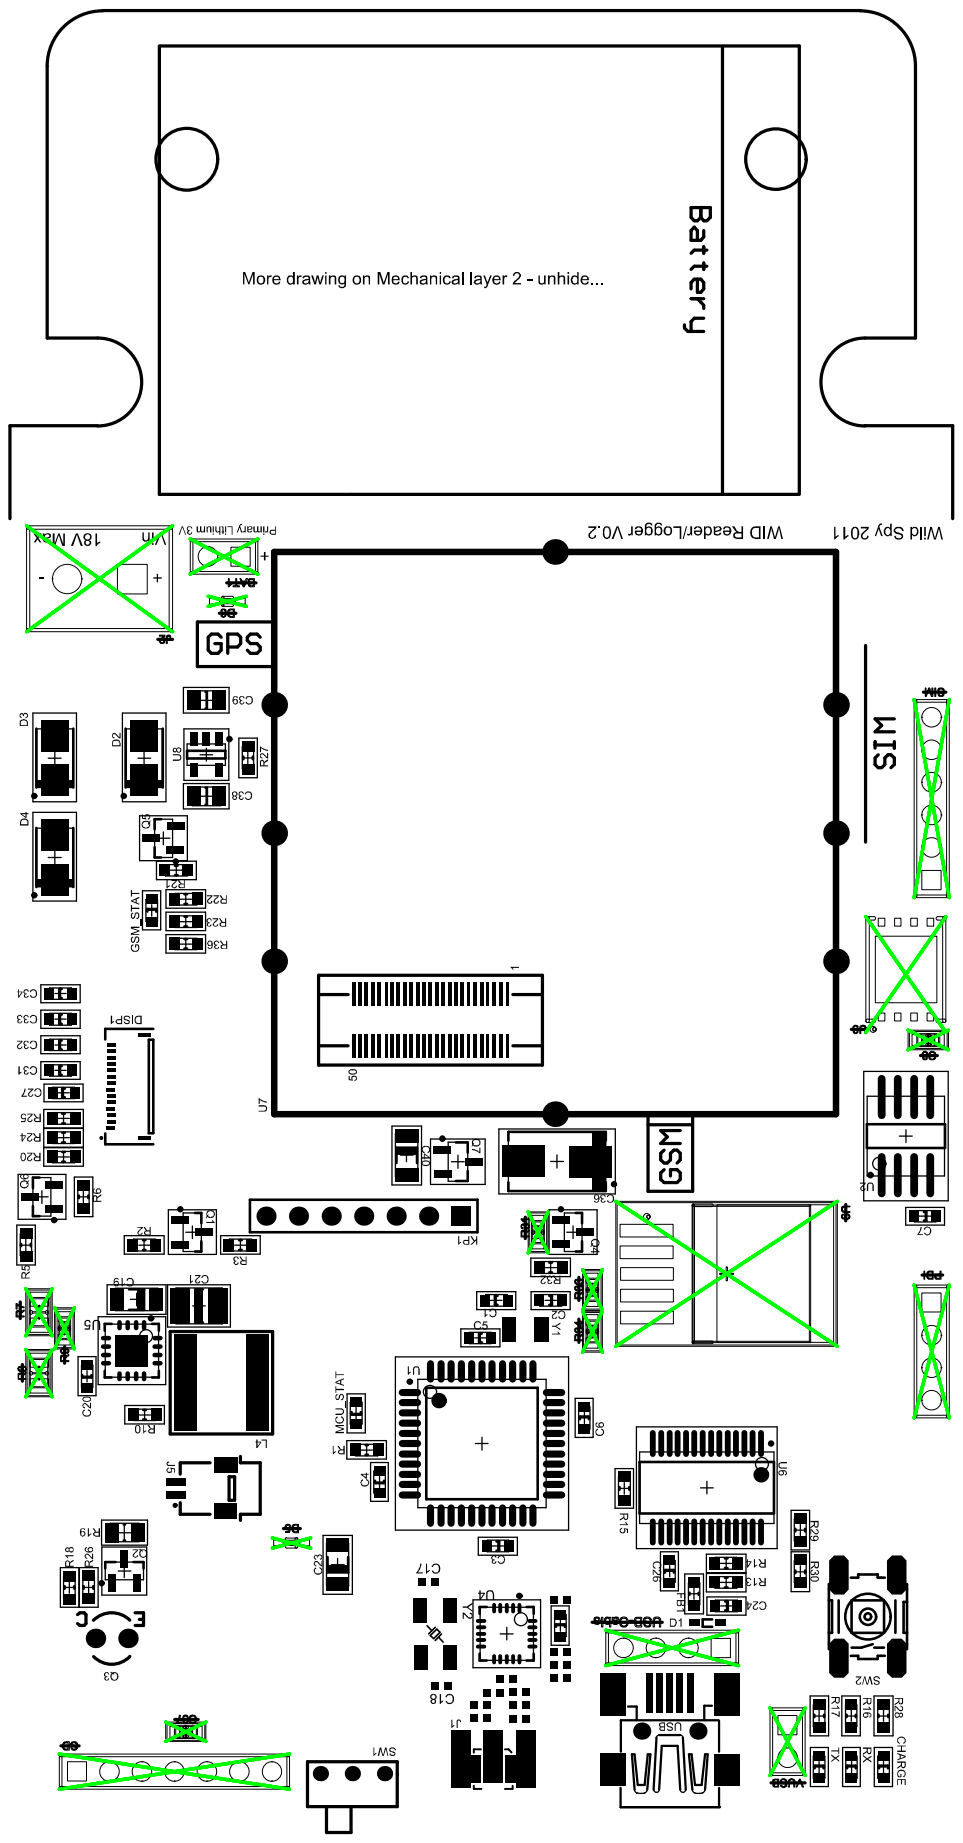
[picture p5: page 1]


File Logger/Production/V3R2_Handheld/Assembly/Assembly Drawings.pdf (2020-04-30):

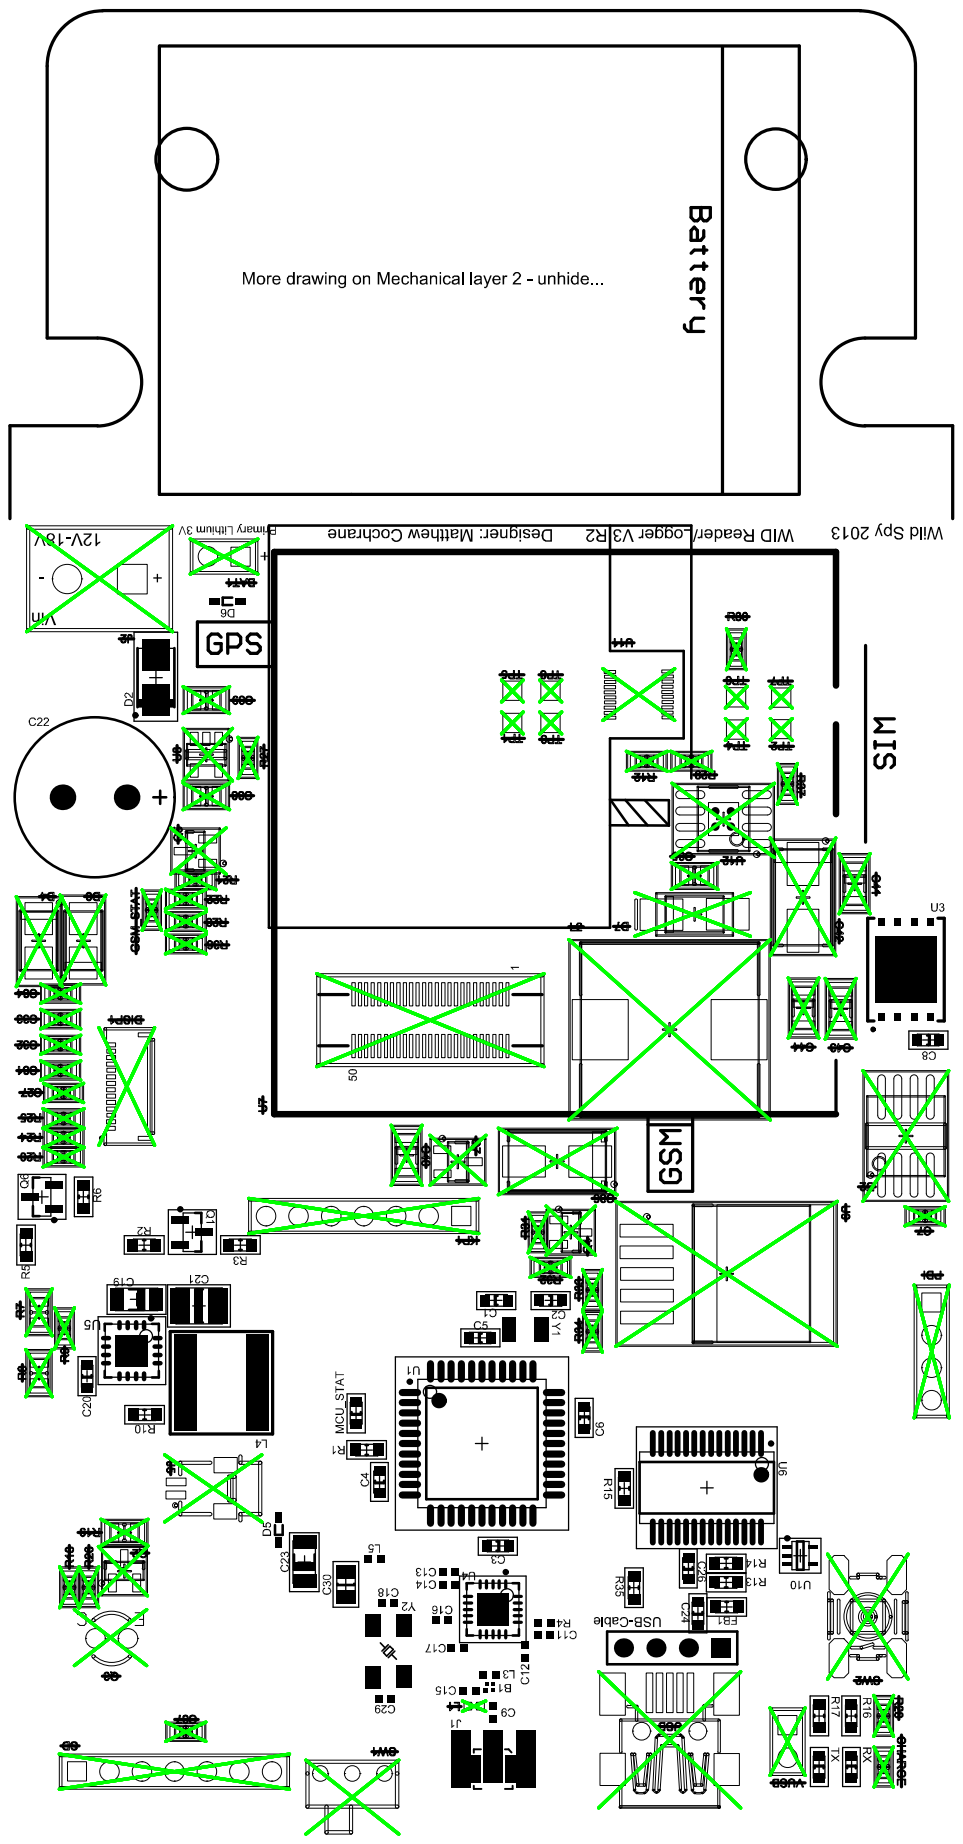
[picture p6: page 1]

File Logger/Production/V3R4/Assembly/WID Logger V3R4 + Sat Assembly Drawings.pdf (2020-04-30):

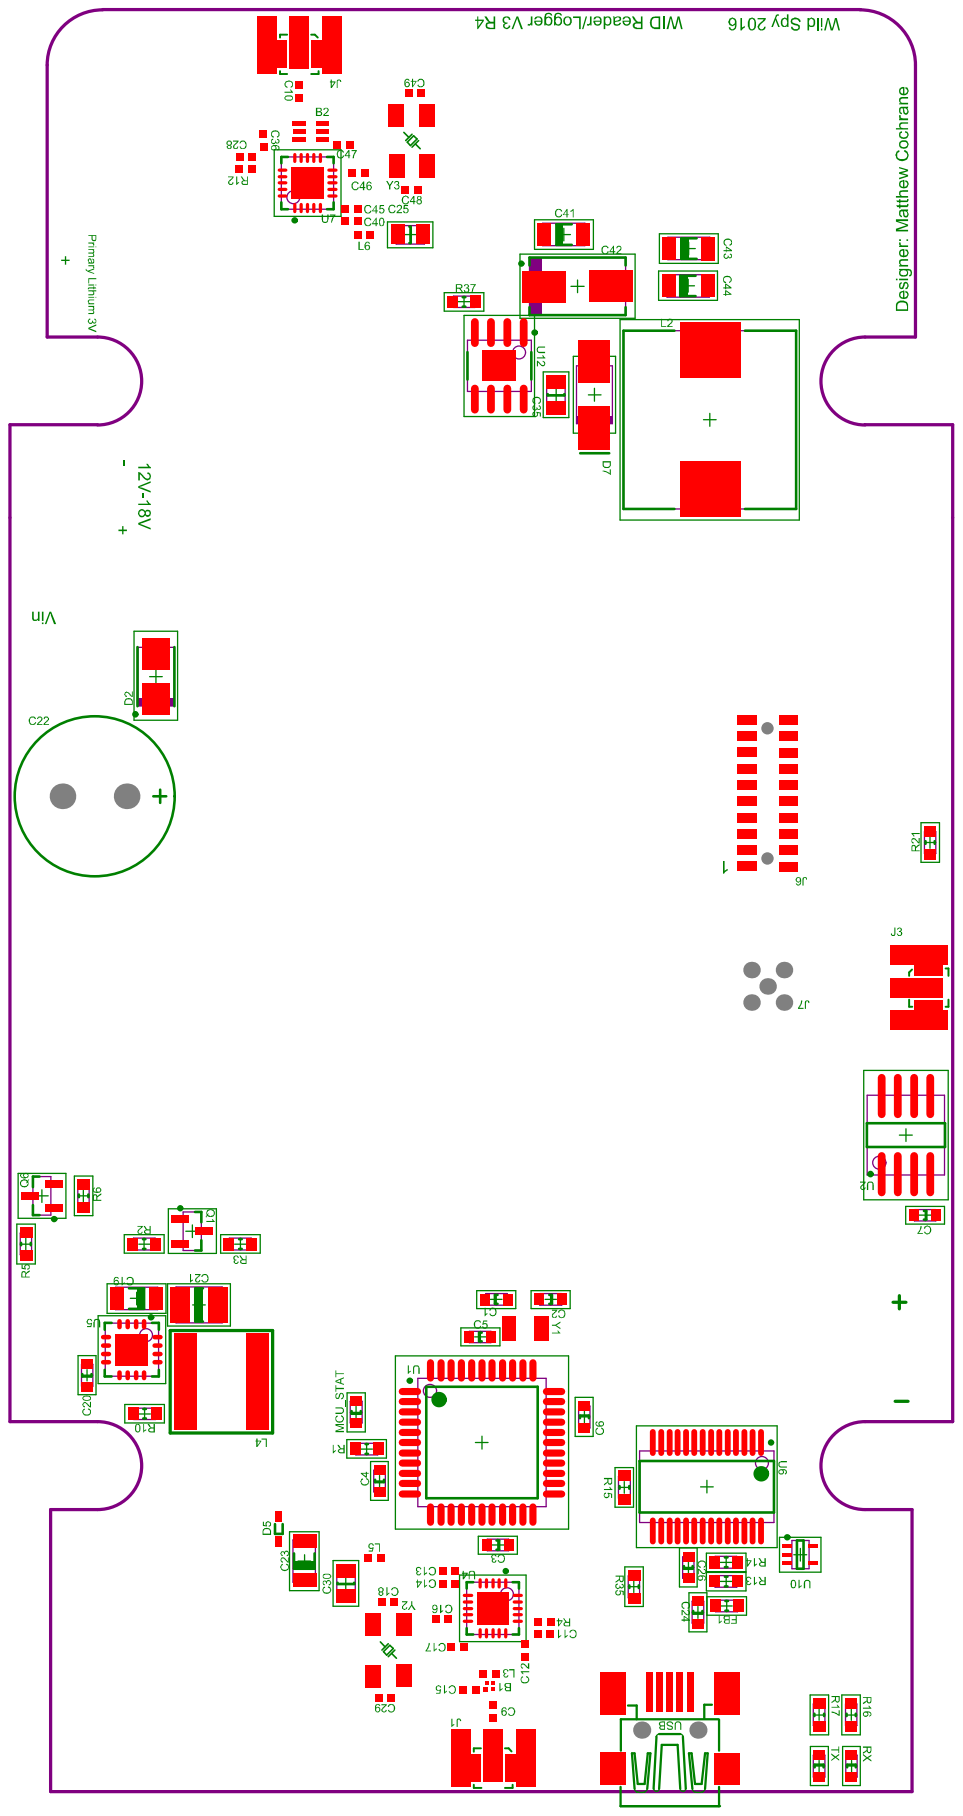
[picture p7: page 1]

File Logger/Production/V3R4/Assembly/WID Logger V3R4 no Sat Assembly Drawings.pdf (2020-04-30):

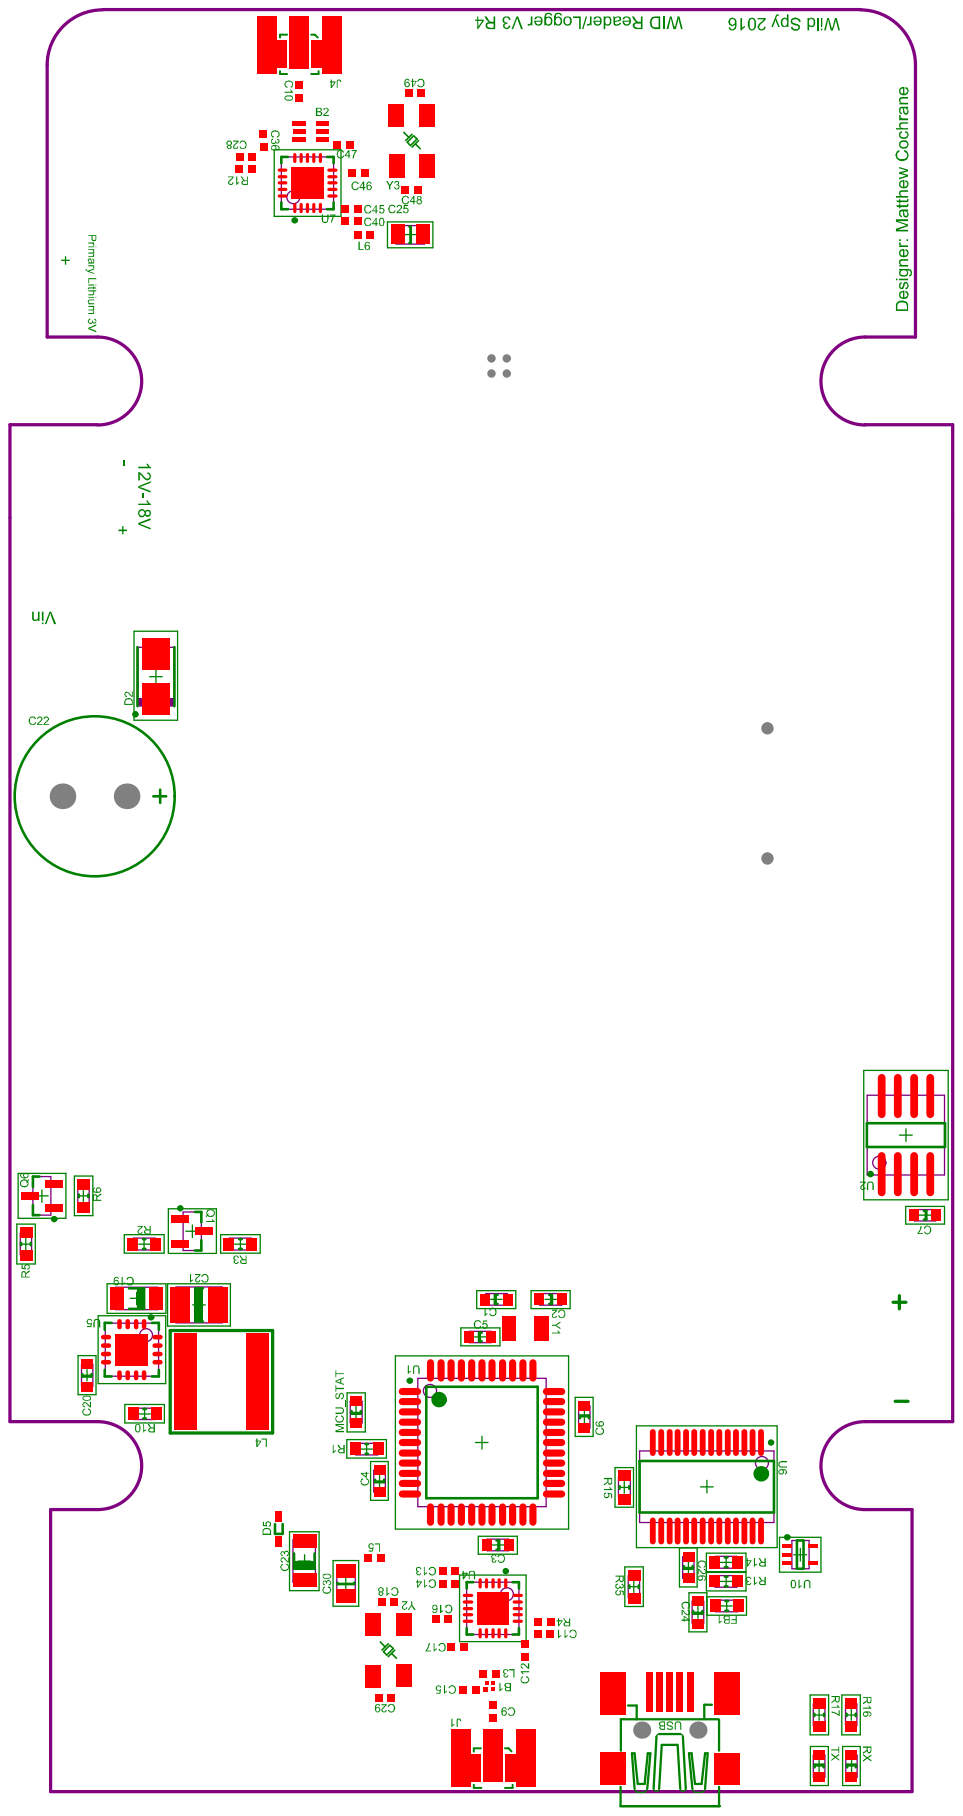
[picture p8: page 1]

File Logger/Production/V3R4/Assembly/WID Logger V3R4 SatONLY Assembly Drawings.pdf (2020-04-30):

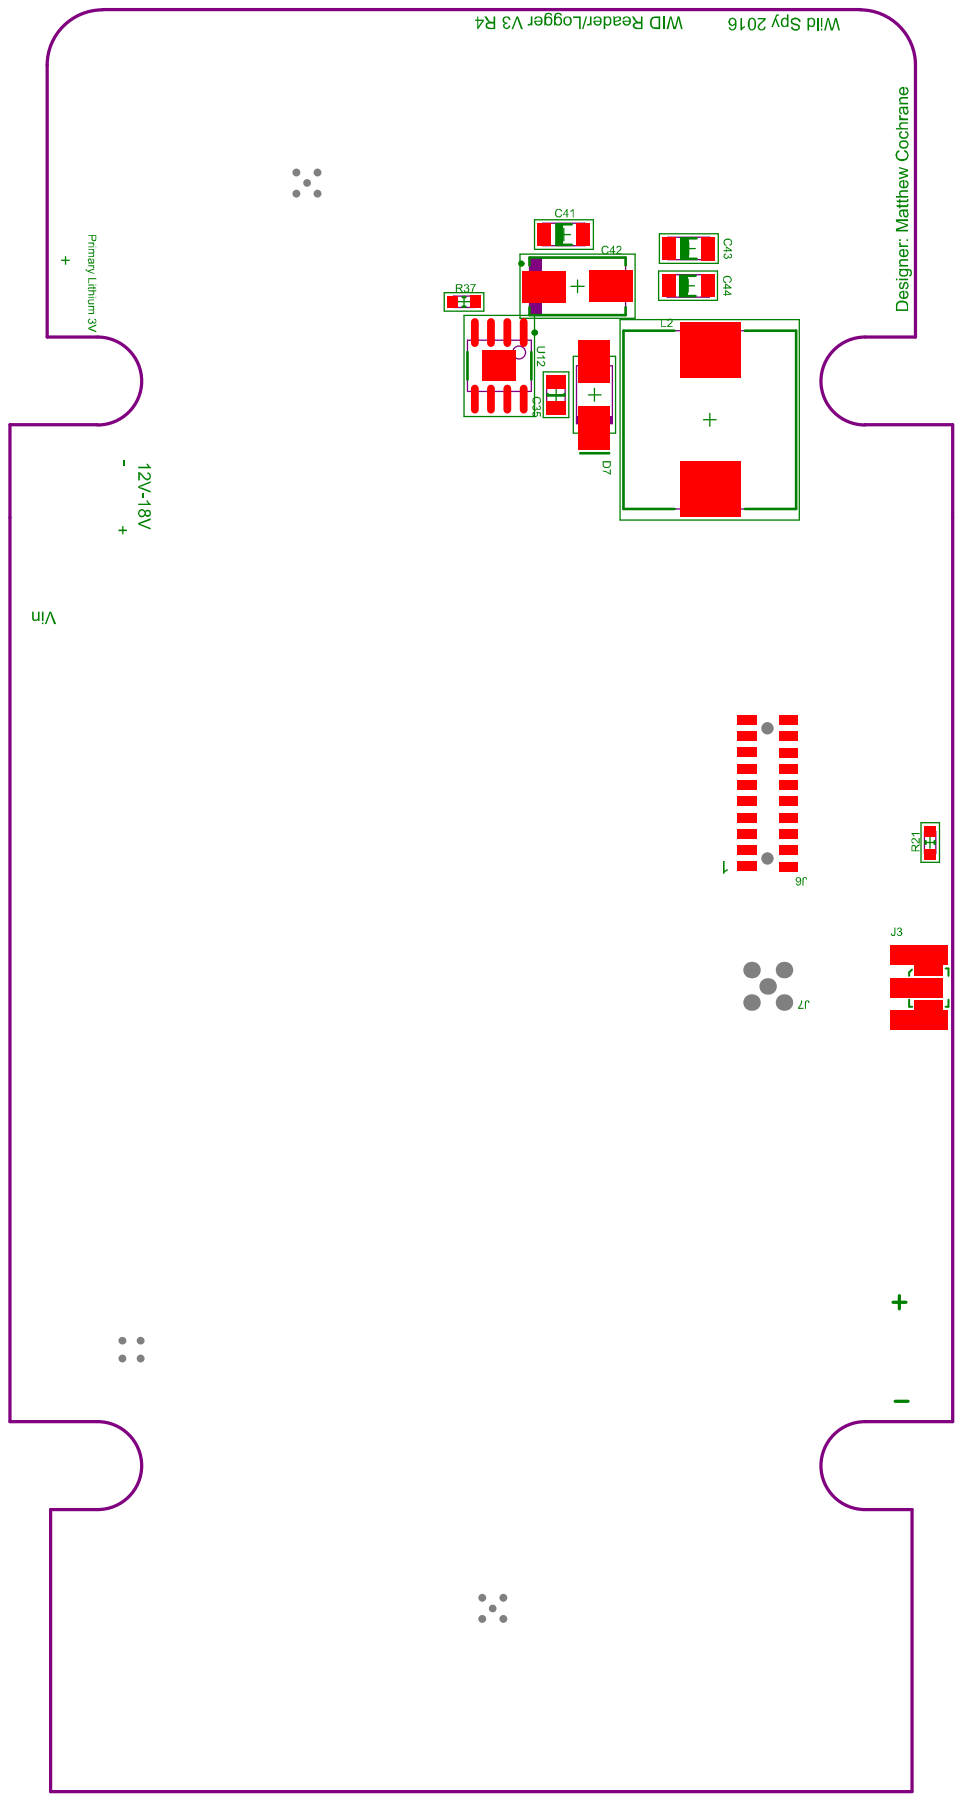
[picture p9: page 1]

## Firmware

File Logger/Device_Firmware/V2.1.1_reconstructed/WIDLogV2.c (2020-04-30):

/* This file has been prepared for Doxygen automatic documentation generation.*/
/*! \file *********************************************************************
 *
 * \brief  WID Logger main source code file.
 *
 *      This file contains the main function as well as the majority of the 
 *		device specific code for the WID Logger.
 *
 * \par Documentation
 *      No further documentation as of yet.
 *
 * \author
 *      Matthew Cochrane \n
 *      Wild Spy
 *
 * $Revision: 0 $
 * $Date: 01/10/2011 $  \n
 *
 *****************************************************************************/

#include "WIDLogV2.h"

uint8_t deadByte;
char s[80];					
//uint8_t myRF_ID[5];						//!<ID on the nordic chip default = {0xE6,0xE6,0xE6,0xE6,0xE6};
//uint8_t myRF_Chan = 2;					//!<Channel on the nordic chip
//char setting_DeviceName[20] = "TestLogger";		//!<Used to ID the logger 19 characters long (20 with the the '\0')

volatile uint16_t timer10ms = 0;		//!<Used to keep track of how many 10ms blocks have passed since the 10ms timer was started.

volatile uint8_t Wakeup_Source = WAKEUP_SOURCE_NONE;	//!<Holds information on what source woke up the device from sleep mode.

//uint32_t RecordCount = 0L;			//!<No. of records in dataflash
uint8_t gotRecCnt = 0;					//!<Have we found the record count yet?
uint8_t TagUpdate = 0;					//!<Counter.. when it gets to 0, the tagupdate function is executed
uint8_t RF_Cal_Cntr = 0;				//!<Counter.. when it gets to 0, the RF segment is re-calibrated
uint8_t RF_CalClr_Cntr = 0;				//!<Counter.. when it gets to 0, the RF segment is re-calibrated
volatile uint8_t secCntr = 0;

uint8_t Startup = 1;					//!<About to startup?

uint8_t CheckBatVolt = 0;				//!<Counter for checking battery voltage (checks every 5? seconds)
float tmpBatV;							//!<The last read battery voltage.

RTC_Time_t RTC_c_Time;					//!<RTC time -> real time stored here.
RTC_Time_t RTC_Period;					//!<Time that elapses per RTC period (1 second)

//RTC_Time_t Send_Data_GPRS_Next;		//!<Next time to attempt to send an email
RTC_Time_t Send_Data_GPRS_Next_Real;	//!<Next scheduled time to send an email
//RTC_Time_t Send_Data_GPRS_Period;		//!<An email is scheduled to be sent once every period
uint8_t Send_Data_GPRS_Retries_Remaining = SEND_DATA_GPRS_RETRIES_MAX;	//!<Number of retries remaining before aborting this email and waiting for next scheduled send email time

//RTC_Time_t RecCount_LastSave;			//!<Time when RecordCount was last saved to EEPROM

uint8_t TagDispMode = 1;				//!<How tags are displayed (None (1), show ID only (2), ID and date/time or ID(3), Date/Time and Address(4))

uint8_t bBak_Mode = 0;					//!<Are we in battery backup mode?
uint8_t bBak_Reason = BBAK_REASON_NONE;	//!<Why are we in battery backup mode?
uint8_t PC_saved[3];					//!<Saved address of Program Counter (pointer to address just before program goes to sleep) used to unsafely abort all operations and put the device to sleep immediately!
uint16_t SP_saved;						//!<Saved stack pointer address, used in conjunction with PC_saved variable above.
volatile uint8_t batBakTrig = 2;		//!<Variable used in managing battery backup modes

int ADCOffset = 0;						//!<Offset of the ADC (see datasheet on ADC offset)
//uint8_t PowerDown = 0;				//!<Flag used to tell the unit to power down when appropriate
uint8_t setting_LoggingEnabled;// = 1;	//!<Is logging enabled? Can still use as tracking device but won't save to flash (initially set to 1 (GUI_LOGSTATEDIT_DISABLED)
uint8_t EnterMobCommsBridgeMode = 0;	//!<Set in the SerComms library, tells the logger to enter GM862 or Iridium Bridge mode which can be exited by sending 0x03 from the computer
uint8_t EnterMobCommsConfigMode = 0;

char setting_Filter[8] = {'*','*','*','*','*','*','*','*'};	//!<Filter String
uint32_t FilterCode;								//!<Filter Code
uint32_t FilterMask;								//!<Used to 

//Variable declarations (not definitions.. they are defined in other c files)
extern ListStruct_t MList_Data[LISTMAXSIZE];		//!<From M_List.c
extern int MList_Count;								//!<From M_List.c
extern uint32_t records_sent_already;				//!<From MX_GM862.c
extern char setting_EMAILTOADD[60];					//!<From MX_GM862.c
extern char setting_GPRSAPN[30];					//!<From MX_GM862.c
extern char setting_GPRSUSERID[30];					//!<From MX_GM862.c
extern char setting_GPRSPASSW[30];					//!<From MX_GM862.c

ISR(RTC_OVF_vect) {
	//PORTC.OUTSET = (1<<1);
	Wakeup_Source |= WAKEUP_SOURCE_RTC;
	AddTimes(&RTC_c_Time, &RTC_Period);
	secCntr++;
}

ISR(PORTE_INT0_vect) {
	//USB plugged in/removed (both events trigger the interrupt)
	CheckBatVolt = BATVOLTCHECK;
	Wakeup_Source |= WAKEUP_SOURCE_RTC;	//so that we do RTC wake checks
	if (USART_USB_IN) {
		//Plugged in
		USART_Setup(&PORTC, &USARTC0, 176, -5, 0);
		//PORTC.PIN2CTRL = PORT_OPC_TOTEM_gc;
		//PORTC_OUTCLR = (1<<2);
	} else {
		//Unplugged
		PORTC.DIRSET = ((1<<2)|(1<<3));
		PORTC.OUTSET = ((1<<2)|(1<<3));
		//PORTC.PIN2CTRL = PORT_OPC_TOTEM_gc;
		USARTC0.CTRLB = 0x00;
	}
}

ISR(PORTB_INT0_vect) {//, ISR_NAKED) {
	//Main Battery Removed/Power lost

	//DO NOT TOUCH THIS FUNCTION!!!!!
	//DO NOT ADD ANY VARIABLES, DON'T CHANGE ANY CODE...
	//JUST DONT FUCKING TOUCH IT!  SHIT WILL EXPLODE!
	uint8_t* RetADD;
	
	//alternate way:
	//RetADD = (uint8_t*)((SPH<<8)+SPL+17);
	
	//Interesting to note that on startup.. not sure when.., but this interrupt is executed.  I think the only reason that
	//battery backup mode is not entered is because of the 100ms delay and then batteryGood re-check in the EnterBatBakMode()
	//function.. I guess that means that that bit of code works quite well!
 
	//Just assume a hard off... if it's plugged in the nordic chip will keep running. This is OK.
	//Otherwise we need to make sure that we handle the case that the USB power could be lost while
	//shutting down the peripherals.  Unlikely, but possible.
	if (bBak_Mode == 0 && bBak_Reason == 0) {
		if (EnterBatBakMode(BBAK_REASON_NO_BAT)) {
			return;
		}
	//Can't abort this function.. we we can but if we do we need to put all the registers and the stack back to normal first!
	//Just disable the interrupt during sections of code where you don't want it to execute.
	} else {
		//reti();
		//abort
		return;
	}
	//if we canceled in EnterBatBakMode()
	if (bBak_Mode == 0 && bBak_Reason == 0) {
		//reti();
		//abort
		return;
	}

	//if we get here we want to hard abort!
	//Set return address to Saved Program Counter Address
	//Note that it doesn't matter what other crap is on the stack if you use reti(), it just uses the top of the stack
	//as the return address
	RetADD = (uint8_t*)((SPH<<8)+SPL);
	*(RetADD+0) = PC_saved[0];
	*(RetADD+1) = PC_saved[1];
	*(RetADD+2) = PC_saved[2];
	reti();
	
	//alternate way:
	//*(RetADD+0) = PC_saved[0];
	//*(RetADD+1) = PC_saved[1];
	//*(RetADD+2) = PC_saved[2];
	//return;
	
}

ISR(PORTC_INT0_vect) {
	Wakeup_Source |= WAKEUP_SOURCE_USART;
}

ISR(PORTD_INT0_vect) {
	Wakeup_Source |= WAKEUP_SOURCE_CC2500;
}

ISR(TCC0_OVF_vect) {
	//10ms Timer update.
	cli();
	if (timer10ms) timer10ms--;
	else {
		TC0_ConfigClockSource(&TCC0, TC_CLKSEL_OFF_gc);
		TCC0.INTCTRLA = TC_OVFINTLVL_OFF_gc;
	}
	sei();
}

//! Main function
/*!
  A more elaborate description. (can be multiple lines).
  \return 0
*/
int main() {
	
	SAVESP();
	PC_saved[0] = 0;
	PC_saved[1] = 0;
	PC_saved[2] = 0;

	SetupHardware();
	
	while (1) {
		//RecordCount = 200000UL;
		//Set restore point...
		if (batBakTrig == 2) {
			SAVESTATE();
			if (batBakTrig == 1) {
				//Restore Stack Pointer
				cli();
				SPH = (uint8_t)(SP_saved>>8);
				SPL = (uint8_t)(SP_saved);
				sei();
			}
			batBakTrig = 0;
		}

		//Clear Nordic IRQ flag
		CC_PORT.INTFLAGS = (1<<0);
		//Go to sleep
		set_sleep_mode(SLEEP_SMODE_PSAVE_gc);
		MCU_STAT_LED_OFF();
		sleep_mode();

		if (bBak_Reason == BBAK_REASON_NONE) {
			MainLoop_Active_Mode();
		} else if (bBak_Reason == BBAK_REASON_NO_BAT) {
			//We are in battery backup mode
			MainLoop_BatBackup_NoBat_Mode();
		} else if (bBak_Reason == BBAK_REASON_LO_BAT) {
			MainLoop_BatBackup_LoBat_Mode();
		}
	}

	return 0;
}

//! Brief Description
/*!
  A more elaborate description. (can be multiple lines).
  \return Desctiption as void 
*/
void MainLoop_Active_Mode() {
	MCU_STAT_LED_ON();
			
	if (Startup) {
		//Stuff to do on startup!!
		//TODO[ ]: TEST AGAIN THAT THIS TURNS OFF WHEN DONE!!!
		//TODO[ ]: uncomment the below lines!!
		//GM862_Unit_On(1);
		//GM862_Unit_Off();
		SAVE_SYS_MSG(SYS_MSG_PWR_ON,0);
		
		tmpBatV = CheckBatteryVoltage();
				
		USART_printf_P(&USARTC0, "RecordCount: %lu\r\n", RecordCount);
		USART_tx_String_P(&USARTC0, PSTR("Going to sleep. Turn device on for serial Comms.\r\n"));
		_delay_ms(2);
	
		Startup = 0;
	}

	//This code just ignores the 'false byte' received by the USART
	//receives upon waking up from battery backup mode.
	if (Wakeup_Source & WAKEUP_SOURCE_PWR) {
		Wakeup_Source &= ~(WAKEUP_SOURCE_PWR);
		Wakeup_Source &= ~(WAKEUP_SOURCE_USART);
	}

	//Pretty much just for PrintRTC and TagUpdate stuff
	//The actual time updating is handled in the ISR
	if (Wakeup_Source & WAKEUP_SOURCE_RTC) {
		Wakeup_Source &= ~(WAKEUP_SOURCE_RTC);
		RTCWakeChecks();
	}

	//TODO[ ]: Consider removing the loop or putting a limit to the number of
	//		   loops as otherwise bombardment of tags could cause the device to
	//		   stop responding (get stuck in the below loop and never service
	//		   the USART.
	//CC - is GD0 (IRQ) low?, if so, do work!
	//uint8_t stat = 0;
	//while (CC_PORT.IN & (1<<CC_GD0)) {
	if (Wakeup_Source & WAKEUP_SOURCE_CC2500) {
		doRFWork(TagDispMode);
		Wakeup_Source &= ~(WAKEUP_SOURCE_CC2500);
		//stat = cc_read_reg(TI_CCxxx0_MARCSTATE);
		
		//USART_printf_P(&USARTC0, "CC_STATE: %lu\r\n", stat);
		//_delay_ms(2);
	}
	//Wakeup_Source &= ~(WAKEUP_SOURCE_CC2500);

	//USART stuff.  This needs to be last.
	if (Wakeup_Source & WAKEUP_SOURCE_USART) {
		//ShowMenu();
		SerCom_err_t tmpErr;
		while (USART_rx_Byte_nb(&USARTC0, &deadByte) == USART_err_Success);
		MCU_STAT_LED_ON();
		if ((tmpErr = Ser_CMDHandler(&USARTC0)) != SerCom_err_Success) {
			Wakeup_Source &= ~(WAKEUP_SOURCE_CC2500);
		}
		Wakeup_Source &= ~(WAKEUP_SOURCE_USART);
		MCU_STAT_LED_OFF();
	}
	
	if (EnterMobCommsBridgeMode) {
// 		GM862_HW_On();
// 		//GM862_Unit_On(1);
// 		//GM862_SendEmail();
// 		GM862_BridgeMode();
// 		GM862_Unit_Off();

		//Iridium_HW_On();
		Iridium_SetupHardware();
		Iridium_Unit_On();
		Iridium_BridgeMode();
		Iridium_Unit_Off();

		EnterMobCommsBridgeMode = 0;
	}
	
	if (EnterMobCommsConfigMode) {
		USART_tx_String_P(&USARTC0, PSTR("Configure Iridium...\r\n")); //GM862...\r\n"));
		//Iridium_HW_On();
		Iridium_SetupHardware();
		Iridium_Unit_On();
		Iridium_ConfigureModule();
		Iridium_Unit_Off();
		USART_tx_String_P(&USARTC0, PSTR("Iridium Configure Done.\r\n"));//GM862 Configure Done.\r\n"));
		_delay_ms(2);
		EnterMobCommsConfigMode = 0;
	}
	
}

//! Brief Description
/*!
  A more elaborate description. (can be multiple lines).
  \return Desctiption as void 
*/
void MainLoop_BatBackup_NoBat_Mode() {
	if (PWR_GOOD) {
		//bBak_Reason = BBAK_REASON_NONE;
		//batBakMode = 0;
		//if batbak interrupt was called while we were waking up, exit!
		//Wakeup_Source |= WAKEUP_SOURCE_PWR;
		if (WakeFromBatBakMode() == 0) {		
			if (!Startup) {
				if (Iridium_Unit_On(1) >= 0) {
					Iridium_Unit_Off();
					//Log record.. time WAS updated from GSM
					SAVE_SYS_MSG(SYS_MSG_WAKE_UD_TIME, 0);
				} else {
					//Log record.. time was NOT updated from GSM
					SAVE_SYS_MSG(SYS_MSG_WAKE_NOTIME, 0);
				}
			}
			RTC_Time_t tmpTime;
			TimeAfterTime(&RTC_c_Time, &tmpTime, 0, 0, 0, 0, 15, 0);
				
			if (FirstTimeGreaterOrEqualTo(&tmpTime, &Send_Data_GPRS_Next)) {
				CopyTime(&tmpTime, &Send_Data_GPRS_Next);
				ReelInTheYears();
			}			

			_delay_ms(1);
			USART_tx_String_P(&USARTC0, PSTR("Wake from bat back mode.\r\n"));
			_delay_ms(2);
		}		
	}
}
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

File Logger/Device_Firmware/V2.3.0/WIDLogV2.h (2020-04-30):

/*
 * WIDLogV2.h
 *
 *  Created on: 06/08/2010
 *      Author: Matthew Cochrane
 */
/* This file has been prepared for Doxygen automatic documentation generation.*/
/*! \file *********************************************************************
 *
 * \brief  WID Logger main source code header file.
 *
 *      This file contains the macros function definitions and defines that are
 *		to be used in the WIDLogV2.c file.
 *
 * \par Documentation
 *      No further documentation as of yet
 *
 * \author
 *      Matthew Cochrane \n
 *      Wild Spy
 *
 * $Revision: 0 $
 * $Date: 01/10/2011 $  \n
 *
 *****************************************************************************/

#ifndef WIDLOG_H_
#define WIDLOG_H_

#define F_CPU 12000000UL

#include <stddef.h>
#include <stdlib.h>
#include <avr/io.h>
#include <avr/sleep.h>
#include <util/delay.h>
#include <util/crc16.h>
#include <avr/pgmspace.h>
#include <avr/interrupt.h>
#include "Libs/clksys_driver.h"
#include "Libs/MX_NRF24L01.h"
#include "Libs/MX_USART.h"
#include "Libs/MX_SerFlash.h"
#include "Libs/MX_RTC.h"
#include "Libs/eeprom_driver.h"
#include "Libs/TC_driver.h"
#include "Libs/M_List.h"
#include "Libs/MX_GM862.h"
#include "Libs/CC2500.h"
#include "Libs/CC110L.h"
#include "Libs/CC110LB.h"
#include "Libs/SettingsManager.h"
#include "Libs/WarningFlasher.h"
#include "Libs/InterLoggerRx.h"
#include "Libs/MX_Iridium9603.h"
#include "Strings.h"
#include "Libs/M_CountList.h"
#include "Libs/ErrorCorrection.h"
#include "Libs/cc110LTester.h"
#include "Libs/WakeupSource.h"

//Defines:
#define BBAK_REASON_NONE				0
#define BBAK_REASON_SOFT_OFF			1
#define BBAK_REASON_LO_BAT				2
#define BBAK_REASON_NO_BAT				3

#define RF_DISP_NONE					0
#define RF_DISP_SINGLETAGMODE			1
#define RF_DISP_TAGID					2
#define RF_DISP_TAGIDTIME				3
#define RF_DISP_TAGIDTIMEADD			4

enum SysClk_Speed {
	CLK_SPD_32MHz = 0,
	CLK_SPD_12MHz_SETUP,
	CLK_SPD_12MHz_SWITCH
};
//#define CLK_SPD_32MHz					1
//#define CLK_SPD_12MHz_SETUP			2
//#define CLK_SPD_12MHz_SWITCH			3

//Saved to Flash when certain events occur (flags = 0x02 = 0b10)
//C -> Command Nibble, D -> Data Nibble
//										0xCCDDDDDD
#define SYS_MSG_PWR_ON					0x00000000L
#define SYS_MSG_WAKE_NOTIME				0x01000000L
#define SYS_MSG_WAKE_UD_TIME			0x02000000L
#define SYS_MSG_SEND_EMAIL_FAIL			0x03000000L //Data = number of attempts
#define SYS_MSG_SENT_EMAIL				0x04000000L	//Data = number of attempts
#define SYS_MSG_SEND_EMAIL_ATTEMPT		0x05000000L	
#define SYS_MSG_UPDATED_TIME			0x06000000L //Data = source

#define SYS_MSG_UPDATE_TIME_SRC_GSM		0x01
#define SYS_MSG_UPDATE_TIME_SRC_PC		0x02

#define USART_TIMEOUT					15000	//wait 15 seconds
#define TAGLISTUPDATE					30		//in seconds
#define RFCALUPDATE						5		//in seconds
#define BATVOLTCHECK					10		//in seconds
#define SEND_DATA_GPRS_RETRIES_MAX		3
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

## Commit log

2020-04-30 Initial commit of logger files
    [LoggerV2_Ser_Cmds.xlsx, rnd_gen_test.xlsx]
2020-04-30 Added logger production files
    [WIDLogger.GBL, WIDLogger.GBS, WIDLogger.GKO, WIDLogger.GTL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]
2020-04-30 Added Atmel MCU tag production files
    [WID BOM.xlsx, Wireless ID.GBL, Wireless ID.GBO, Wireless ID.GBP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]
